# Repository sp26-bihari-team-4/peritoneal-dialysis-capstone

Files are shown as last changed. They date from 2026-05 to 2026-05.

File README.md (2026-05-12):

# Repositionable Catheter for Peritoneal Dialysis

This repository contains the software and circuit schematics created by Team 4 for our CSE capstone. At a high level, our system allows a user to control the power provided to two nitinol wires to heat them up and induce them to change shape. If embedded into a catheter, this would cause the catheter to move; in principle, this would allow repositioning of the catheter after it's been implanted into a patient.

The following sections describe how to set up the software environment, important commands, our software architecture, our circuit design, and our CI/CD setup.

## Software Environment Setup

You can get the code in this repository with Git (i.e., `git clone`). Alternatively, you can download and extract the ZIP file from GitHub.

### Compiling and Flashing

To compile the software and flash it to a microcontroller (Arduino), you need to have PlatformIO installed. PlatformIO has their own install instructions in [their docs](https://docs.platformio.org/en/stable/core/installation/methods/index.html), but the following are our recommended methods. Also, please note that links to the PlatformIO docs will point to the latest stable version, which may be different than the version used by this project.

#### Linux/Unix

If your distro's package repository has PlatformIO or PlatformIO Core version 6.1, we recommend installing and using that. Otherwise, install Python 3.14, optionally [set up a virtual environment](https://docs.python.org/3/library/venv.html), and install PlatformIO from PyPI:

```sh
pip install platformio==6.1.19
```

#### macOS

For Mac, we recommend using the [Homebrew package manager](https://brew.sh/). With Homebrew installed, just run:

```sh
brew install platformio@6.1.19
```

#### Windows

PlatformIO is implemented as a Python package, so you'll first need to install Python. We recommend using the Python Install Manager, which you can install with the following PowerShell command:

```powershell
winget install Python.PythonInstallManager
```

With that installed, you can run the following command to get Python 3.14:

```powershell
pymanager install 3.14
```

Next you can install the PlatformIO package with pip:

```powershell
python -m pip install platformio==6.1.19
```

The above command will likely print some warnings about needing to add a directory to your PATH variable. Copy the path to the directory it gives you (it should end with `Scripts`), and follow [a tutorial like this](https://www.wikihow.tech/Add-Path-on-Windows) to add it to your User Path variable. Note that you'll need to restart PowerShell for this change to take effect.

#### Run PlatformIO

With PlatformIO installed, you should be able to run the following command to compile the project:

```sh
pio run -e uno
```

The result should be something like:

```
Environment    Status    Duration
-------------  --------  ------------
uno            SUCCESS   00:00:01.232
```

With an Arduino connected to your computer, you can run the following command to compile and flash the software to the microcontroller:

```sh
pio run -e uno -t upload
```

### Development Dependencies

There are a couple other programs you'll want installed if you plan on making any changes to the code.

#### GCC

While PlatformIO manages the compiler for the microcontroller, our unit tests run natively and require GCC (specifically `g++`) to be installed. On Linux, if you don't already have GCC, it's almost certainly available in your distro's package repository. On macOS, you can install GCC from Homebrew with `brew install gcc`.

On Windows, the easiest way to get GCC is to install a [Mingw-w64 distribution](https://www.mingw-w64.org/downloads/). A relatively small one is [w64devkit](https://github.com/skeeto/w64devkit/releases/tag/v2.7.0). Just download and extract the x64 archive. The resulting directory should have an executable called `w64devkit.exe`. Running this program will give you a Unix-like shell that includes common tools like GCC and Make. There's also a way to add these programs to your User Path variable, but it's not necessary.

With GCC installed (and available in your shell), you can use the following command to run the unit tests:

```sh
pio test -e native
```

#### Clang Tools

PlatformIO manages an installation of [clang-tidy](https://releases.llvm.org/21.1.2/tools/clang/tools/extra/docs/clang-tidy/index.html), but our linting setup also uses [clang-format](https://releases.llvm.org/21.1.2/tools/clang/docs/ClangFormat.html) (version 21), so it needs to be installed separately.

#### Doxygen

Our documentation is generated with [Doxygen](https://doxygen.nl/index.html). If you want to do that locally, install version 1.16.1 from their site or your preferred package manager. To render many of the graphs/diagrams in the docs, Doxygen requires [`dot`](https://graphviz.org/docs/layouts/dot/) to be available. You can get this utility as part of [Graphviz 14.1.5](https://graphviz.org/download/). Additionally, to render our [software architecture diagram](software-architecture.md), Doxygen needs to be able to run [PlantUML](https://plantuml.com/starting). You can download `plantuml-1.2026.2.jar` from their [GitHub release](https://github.com/plantuml/plantuml/releases/tag/v1.2026.2) and save it to the project root directory. To be able to run the JAR file, you'll need a Java Runtime Environment installed. We recommend installing [an Eclipse Temurin OpenJDK 25 build](https://adoptium.net/installation).

#### KiCad

One last piece of software you might want to install is [KiCad](https://www.kicad.org/) (version 9), which was used to make our circuit schematic. With it installed, you should be able to open the KiCad project file `hardware/capstone.kicad_pro` to see and modify the schematic.

## Important Commands

As mentioned in the setup, you can run the following command to compile the code for Arduino:

```sh
pio run -e uno
```

For convenience, we've added a `compile` target in our Makefile. So with Make installed, you can equivalently run:

```sh
make compile
```

To compile and flash the code to a connected Arduino:

```sh
pio run -e uno -t upload
```

Or equivalently:

```sh
make flash
```

Use one of the following two commands to display the serial console:

```sh
pio device monitor
make serial-console
```

Use one of the following two commands to run our unit tests:

```sh
pio test -e native
make run-tests
```

To run linting:

```sh
pio check -e uno --fail-on-defect high --fail-on-defect medium --fail-on-defect low
```

To check code formatting on all the source files:

```sh
clang-format --dry-run $(find src lib include test -regex ".*\.\(cpp\|h\)")
```

The previous two commands can be easily run with:

```sh
make lint
```

To automatically fix formatting issues identified by clang-format, run one of the following two commands. However, be warned that it may make unwanted formatting changes to your code.

```sh
clang-format -i $(find src lib include test -regex ".*\.\(cpp\|h\)")
make format
```

To generate the Doxygen documentation site in `doc/html`, simply run:

```sh
doxygen
```

Lastly, if you'd like to remove the compiled PlatformIO builds, run:

```sh
pio run -e uno -t clean
pio run -e native -t clean
```

Or equivalently:

```sh
make clean
```

The PlatformIO CLI has many other useful commands, which are all documented in [the CLI guide](https://docs.platformio.org/en/stable/core/userguide/index.html). Likewise, [clang-tidy](https://releases.llvm.org/21.1.2/tools/clang/tools/extra/docs/clang-tidy/index.html) and [clang-format](https://releases.llvm.org/21.1.2/tools/clang/docs/ClangFormat.html) have many interesting options. We have both of them configured using config files (`.clang-tidy` and `.clang-format`). The clang-format docs are also useful for seeing all the [style options](https://releases.llvm.org/21.1.2/tools/clang/docs/ClangFormatStyleOptions.html).

## Circuit Design

### Overview

The goal of the system is to independently control the shapes of two nitinol wires by heating them to the austenitic phase (or allowing them to cool back to the martensitic phase). In order to complete the martensite-to-austenite transition and induce a shape change, the "Af" transition temperature must be reached. In our wires, this is 45 &deg;C. Since the wires are to be implanted in the body, they will normally be at 37 &deg;C. Therefore, we need to heat the nitinol wires by up to 8 &deg;C.

In our system, this heating is accomplished by passing an electric current through the wires (i.e., [Joule heating][joule-heating]). Two power MOSFETs allow significant power to be delivered to the wires from a voltage source. These MOSFETs are switched on or off by a microcontroller using pulse-width modulation (PWM) to achieve a desired average voltage, which is controlled by two potentiometers. A TFT display shows in real-time the PWM duty cycle of each wire. This duty cycle represents the wire voltage, which is proportional to the square root of the power (and the square root of the rate of temperature increase, assuming no heat loss).

### Detailed Description

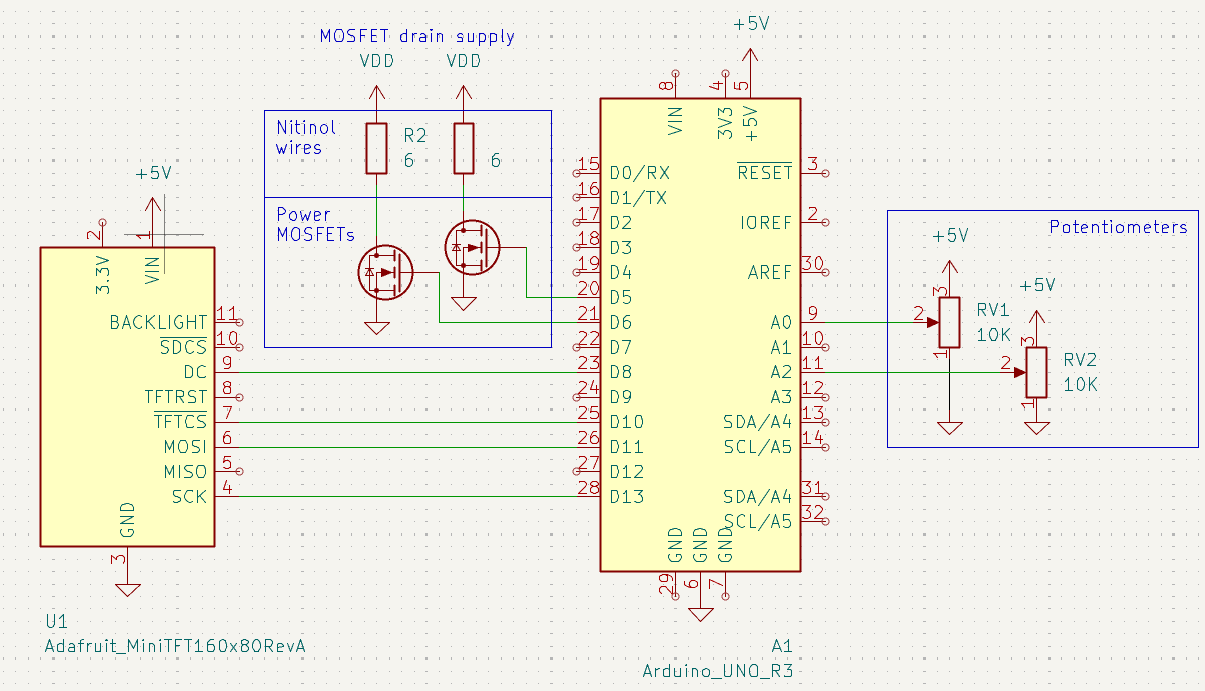
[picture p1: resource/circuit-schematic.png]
The circuit schematic, depicting the Arduino, potentiometers, MOSFETs, and LCD module.


The system is controlled by an [Arduino UNO R3][arduino-uno-r3] microcontroller, which can be programmed and powered via the built-in USB port.

Two 10kΩ rotary potentiometers control the power to the nitinol wires. The resistive track terminals are tied to +5V and (Arduino) GND, and the wiper terminals are tied to analog input pins A0 and A2 of the Arduino; this allows the voltage divider outputs of the potentiometers to be sampled by the Arduino.

The Arduino replicates these input voltages on two digital output pins using PWM. Each digital output is controlled by one analog input; the pair of pins comprise a "channel" that in turn corresponds to one nitinol wire. Channel 1 comprises input A0 and output D5, and channel 2 comprises input A2 and output D6:

|Channel|Input Pin|Output Pin|
|-------|---------|----------|
|1      |A0       |D5        |
|2      |A2       |D6        |

These PWM output pins are used to drive two logic-level MOSFETs ([Infineon IRLZ34N][irlz34n]) that deliver power to the nitinol wires. Each PWM output connects to the gate terminal of one MOSFET. The MOSFET source terminals connect to Arduino GND, and the drain terminals connect to the negative ends of the nitinol wires (the loads). Wiring each MOSFET this way ensures that the gate-to-source voltage ("Vgs") can surpass the threshold voltage ("Vth," approx. 1-2V), which is necessary to conduct current between the drain and source terminals. Indeed, this condition is acheived when the corresponding PWM output is high: the gate will be at 5V, and because the source is 0V (GND), Vgs is 5V&mdash;well in excess of Vth.

While nitinol has a relatively high resistivity, the nitinol wires still don't have a particularly high resistance (around a few ohms, depending on the length and thickness). As a result, for a given voltage across the wires, they'll draw a large amount of current. However, the Arduino 5V line can only provide a few hundred milliamps (depending on the power source). Therefore, an external power supply must be used. The positive terminal should connect to the positive ends of the nitinol wires (labeled VDD in the schematic), and the negative terminal should connect to the MOSFET source terminals (and, by extension, also Arduino GND).

An [Adafruit 0.96" 160&times;80 Color TFT display][tft-display] is used to display the PWM duty cycle of each nitinol wire in real-time. Since the display communicates via SPI, the hardware SPI pins D10, D11, and D13 of the Arduino are tied to the TFTCS, MOSI, and SCK pins, respectively, of the display module. Data and commands are sent via a side channel, from pin D8 on the Arduino to the DC pin on the display. The display is also powered by the Arduino, with VIN and GND tied to the Arduino's +5V and GND, respectively. All other pins on the display are left unconnected (they have internal pull-ups or pull-downs).

[joule-heating]: https://en.wikipedia.org/wiki/Joule_heating
[arduino-uno-r3]: https://docs.arduino.cc/hardware/uno-rev3/
[irlz34n]: https://www.infineon.com/part/IRLZ34N
[tft-display]: https://www.adafruit.com/product/3533

## Software Architecture

The following diagram shows a (slightly editorialized) view of the relationships between all the classes and interfaces we created:

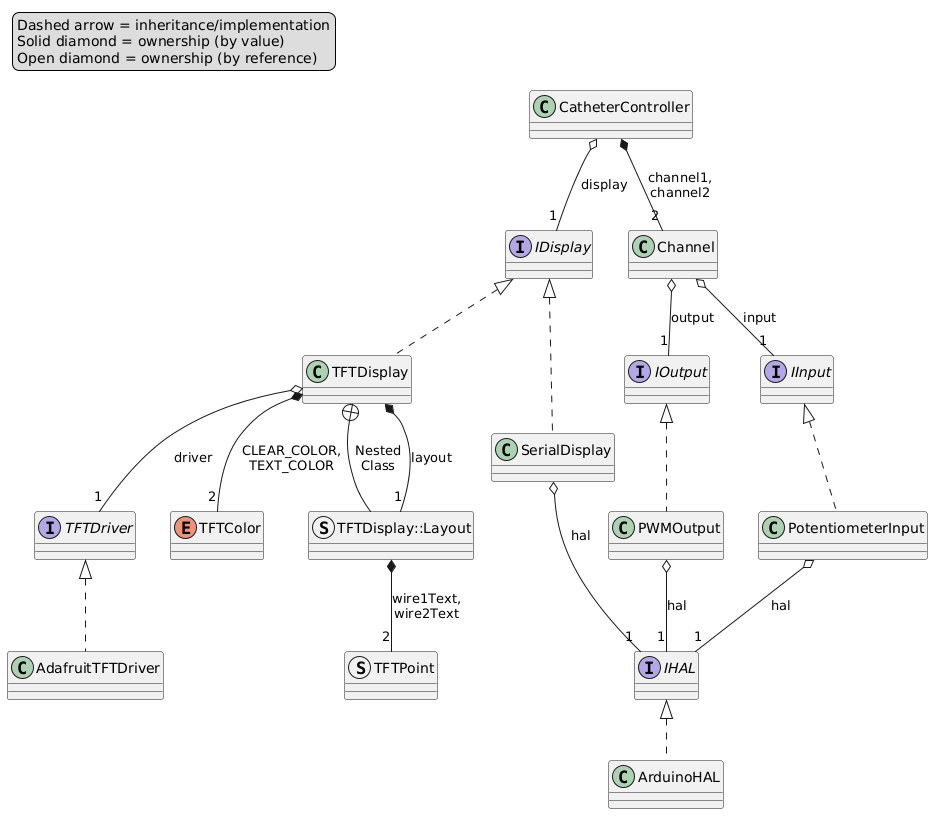
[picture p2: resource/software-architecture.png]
A PlantUML class diagram showing inheritance and ownership between the classes in the codebase


`CatheterController` is our main encapsulating class. It's instantiated by `src/main.cpp` and its `update` method is continually called. `CatheterController` owns a reference to an `IDisplay`, which is an interface defining the functionality of our display classes. `CatheterController` also owns two `Channel` objects, which each represent a pairing of a potentiometer input and a PWM output.

Actually, each `Channel` owns references to an `IInput` and `IOutput`, of which `PotentiometerInput` and `PWMOutput` are the only implementing classes. Without context, this may seem unnecessary, but having interfaces for these classes is useful when it comes to unit testing the `Channel` class, since it allows us to easily mock the input and output objects that `Channel` uses. See the [section below on testing](#testing).

You'll notice that both `PotentiometerInput` and `PWMOutput` own references to an `IHAL` object. We use HAL as an abbreviation for hardware abstraction layer. Like some of our other interfaces, this one only has one implementing class, `ArduinoHAL`. While the other ones were set up like that just for testing/mocking purposes, this setup also facilitates portability. `IHAL` defines all the (non-display) hardware functionality that the rest of the code requires. `ArduinoHAL` implements this functionality using the Arduino framework. In fact, our HAL interface is nearly one-to-one with the Arduino framework, so practically every `ArduinoHAL` method simply calls a corresponding Arduino function. Crucially however, `IHAL` can be implemented for many other microcontrollers or full-on computers (i.e., ESP8266, Raspberry Pi, Teensy, etc.). Setting it up this way allows our software to be ported to new hardware with minimal modifications. Only `IHAL`, `TFTDriver`, and `src/main.cpp` need to be reimplemented to move to a new microcontroller and display. You'll notice that our implementations for these live in the `src` directory, since they're hardware specific; the rest of the code is hardware-agnostic.

Our software's portability is also enhanced by PlatformIO, which is an embedded programming tool that makes it easy to target multiple boards/platforms. In `platformio.ini`, the `uno` environment targets our Arduino UNO and specifies which third-party libraries to compile with. You can also see the `native` environment, which is used for running our unit tests locally. To target a new microcontroller supported by PlatformIO ([there are many](https://docs.platformio.org/en/latest/boards/index.html)), a new environment would need to be added, specifying the platform, board, and framework. PlatformIO would then handle installing the correct compiler and facilitate uploading to the new board.

Like `PotentiometerInput` and `PWMOutput`, `SerialDisplay` also owns a reference to an `IHAL`. `SerialDisplay` is an implementation of `IDisplay` that prints outputs to the microcontroller's serial console. The serial functionality is defined in the HAL, hence the reference to `IHAL`. `SerialDisplay` is great for testing and debugging, but it requires the microcontroller to be connected to a computer to see the console. `TFTDisplay` is a separate implementation of `IDisplay` that supports printing to a physical display, like a TFT LCD. Like all our other classes in `lib`, `TFTDisplay` is hardware-agnostic; the hardware-specific display functionality is encapsulated in the `TFTDriver` interface, which `TFTDisplay` owns a reference to. The only implementing class of `TFTDriver` is `AdafruitTFTDriver`, which is specific to the display model we use. Like with `IHAL`, this structure simplifies the process of moving to a new display, as one would only need to reimplement `TFTDriver`.

To complete this description of the diagram, we'll mention that `TFTDisplay` owns an instance of a nested struct called `Layout`, which in turn owns two `TFTPoint` structs. `TFTDisplay` also owns two instances of the `TFTColor` enumeration. These are all used by `TFTDisplay` to print text in the right places on the display and using the correct colors.

### Testing

Along with aiding our software's hardware compatibility, PlatformIO also manages our testing framework: [GoogleTest](https://google.github.io/googletest/). The main GoogleTest features that we employ are test fixtures and mocks.

A simple example of a test fixture is `SerialDisplayTest` in `test/SerialDisplayTest.cpp`. The former is a class that inherits from the GoogleTest class `testing::Test`. Below the class definition, we use the GoogleTest `TEST_F` macro multiple times. Each of these is treated as an individual test case, named by the second parameter to the macro. Since we pass `SerialDisplayTest` to the macro each time it's used, a new `SerialDisplayTest` object is created before each test case, giving us a fresh copy of all the member variables within it.

Within each test case, you'll notice that we use a macro called `EXPECT_CALL`. This macro is defined by gMock, GoogleTest's mocking library. We recommend reading [the gMock intro](https://google.github.io/googletest/gmock_for_dummies.html) to understand what mocking is, but in short, it allows us to create "fake" versions of classes in order to unit test a class that depends on them. For example, `SerialDisplay` owns a reference to our hardware abstraction layer. In order to test `SerialDisplay` individually (i.e., separately from the HAL), we need to verify that its methods call the HAL methods that we expect with the parameters that we expect. So, we can create a mock implementation of `IHAL` that we pass to `SerialDisplay` instead of a real version like `ArduinoHAL`. gMock does most of the work in filling in this mock class (defined in `test/MockHAL.h`), and it allows us to set expectations on method calls and return expected values from those calls (among other things). In `SerialDisplayTest`, you can see that when we test the `SerialDisplay.update` method, we expect it to call the `IHAL.println` method with specific string values, depending on the numbers passed to it. Here, we use the GoogleTest string matcher, `StrEq`, to tell it to compare the string values instead of the literal `char` pointer values.

Because we've explicitly separated the parts of our codebase that are hardware-specific and hardware-agnostic, we're able to test the latter on any hardware. PlatformIO allows us to define a `native` environment that compiles the code and tests for the local system. By using this, we can run tests without connecting to the actual microcontroller, enabling quick iteration and even continuous integration (see [the section on CI/CD](#cicd)).

## CI/CD

To aid development and usability of this project, we've created a couple of GitHub Actions workflows.

`pio-test.yml` contains one job that compiles and tests the code on every pull request and every push to a main or stage branch. As described in the setup instructions, it uses Python 3.14 and PlatformIO 6.1.19. We've set up this repository so that the main branch can only be edited by making pull requests. Furthermore, the pull requests must be up-to-date with the main branch, and they must pass this workflow (i.e., all the tests pass). In this way, we ensure that any code we merge into main is working and doesn't break any existing functionality.

`lint.yml` runs on all of the same events (all PRs and all pushes to `main` or `stage/**`), but instead lints the code using clang-tidy and clang-format. The clang-tidy job runs the same `pio check` command as described in the [important commands section](#important-commands). The clang-format job uses [a third-party Action](https://github.com/marketplace/actions/clang-format-check?version=v4.16.0) to handle installing and running clang-format. The latter job runs separately on the `src`, `lib`, `include`, and `test` directories to better match the format-checking command given in the important commands section, and to prevent clang-format from checking any unnecessary files.

Lastly, we have `deploy-doxygen-docs.yml`. As the name suggests, this workflow automatically generates the Doxygen docs for every push to main and deploys those docs to GitHub Pages. The link to the docs is in the sidebar of this repo. This workflow uses a mix of `wget` and some third-party Actions to install the correct versions of Doxygen, Java, Graphviz, PlantUML, and KiCad. This allows the docs to contain the most up-to-date software architecture diagram and circuit schematic.

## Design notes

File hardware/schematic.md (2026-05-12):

# Circuit Schematic

The circuit schematic, depicting the Arduino, potentiometers, MOSFETs, and LCD module.

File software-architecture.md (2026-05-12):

```plantuml
@startuml{software_architecture.png}

' Legend
legend top left
Dashed arrow = inheritance/implementation
Solid diamond = ownership (by value)
Open diamond = ownership (by reference)
endlegend

' Interfaces
interface IDisplay
interface IHAL
interface TFTDriver
interface IInput
interface IOutput

' Classes
class SerialDisplay
class TFTDisplay
class ArduinoHAL
class AdafruitTFTDriver
class PotentiometerInput
class PWMOutput
class CatheterController
class Channel

' Structs
struct TFTPoint
struct "TFTDisplay::Layout" as Layout

' Enums
enum TFTColor

' Inheritance/implementation
IDisplay <|.. SerialDisplay
IDisplay <|.. TFTDisplay
IHAL <|.. ArduinoHAL
TFTDriver <|.. AdafruitTFTDriver
IInput <|.. PotentiometerInput
IOutput <|.. PWMOutput

' Ownership (by value)
CatheterController *-- "2" Channel : channel1,\nchannel2
TFTDisplay +-- Layout : Nested\nClass
TFTDisplay *-- "1" Layout : layout
TFTDisplay *-- "2" TFTColor: CLEAR_COLOR,\nTEXT_COLOR
Layout *-- "2" TFTPoint : wire1Text,\nwire2Text

' Ownership (by reference)
CatheterController o-- "1" IDisplay : display
Channel o-- "1" IInput : input
Channel o-- "1" IOutput : output
PotentiometerInput o-- "1" IHAL : hal
PWMOutput o-- "1" IHAL : hal
SerialDisplay o-- "1" IHAL : hal
TFTDisplay o-- "1" TFTDriver : driver

@enduml
```

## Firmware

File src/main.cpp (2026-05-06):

#include <AdafruitTFTDriver.h>
#include <Arduino.h>
#include <ArduinoHAL.h>
#include <CatheterController.h>
#include <TFTDisplay.h>

enum {
	INPUT_PIN_1 = A0,
	INPUT_PIN_2 = A2,
	OUTPUT_PIN_1 = 5,
	OUTPUT_PIN_2 = 6,
	DISPLAY_CS_PIN = 10,
	DISPLAY_DC_PIN = 8,
	BAUD_RATE = 9600,
	DELAY_MS = 100,
};

ArduinoHAL hal(BAUD_RATE);
AdafruitTFTDriver tftDriver(DISPLAY_CS_PIN, DISPLAY_DC_PIN);
TFTDisplay display(tftDriver);
CatheterController controller(
	hal, INPUT_PIN_1, OUTPUT_PIN_1, INPUT_PIN_2, OUTPUT_PIN_2, display
);

void setup() {
	display.initialize();
}

void loop() {
	controller.update();
	hal.delayMs(DELAY_MS);
}

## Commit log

2026-03-09 impl. ArduinoHAL
2026-03-25 fix ArduinoHAL recursion
2026-03-25 ArduinoHAL: explicitly convert digitalRead result
    I just learned that C++ does not define an implicit conversion from
    'int' to an unscoped enum type; you need to use an explicit conversion
    (i.e., cast). There is however an implicit conversion in the reverse
    direction (unscoped enum to 'int'), so the 'digitalWrite'
    implementation is OK.
2026-03-25 Write main.cpp and get program to compile
    Added a needed include to `CatheterController.h` and edited the implementation for `SerialDisplay::update` since Arduino doesn't support floats with `snprintf`.
2026-03-25 Move ArduinoHAL into src so tests can compile
2026-04-03 set pin mode in PotentiometerInput and PWMOutput ctor
2026-04-03 test pin mode setting
2026-04-15 adjust pin assignments for TFT
2026-04-20 Pin PlatformIO version in Action workflows
    Also upgrade to `actions/cache@v5` since v4 uses Node.js 20 which is deprecated and will be removed from Action runners in September.
2026-05-04 add final KiCad project files
    [capstone.kicad_sch]
2026-05-04 add "Circuit Design" section to README
2026-05-04 add circuit schematic to README
2026-05-06 README: apply fixes to circuit description from Dennis
2026-05-06 Render circuit schematic in doc deployment workflow
2026-05-07 polish README circuit section
2026-05-07 Complete software architecture description
    Updated the diagram to include TFTColor and label TFTDisplay::Layout and TFTPoint as structs instead of classes. Added the updated PlantUML code, which I expect will cause a merge conflict with the s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
2026-05-12 Reorder deployment workflow steps to avoid issues with folder permissions
    When run before Doxygen, the "Render circuit schematic" step creates the `doc/html` directory to put the circuit schematic SVG into. For some reason, in the GitHub runner environment, this results in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
